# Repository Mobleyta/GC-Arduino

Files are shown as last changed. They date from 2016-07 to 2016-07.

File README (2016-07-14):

GasChromino Project

The GasChromino Program is an interface program that allows a PC/Mac/Linux system
to communicate with an Arduino that is connected to one or more gas chromatography
instruments.

The project consists of two main programming parts, the Arduino code that is uploaded to
an Arduino Uno (Rev 3) and the python code that is implemented on the computer. Serial
interface through a USB port allows the two programs to communicate.

Instructions for Installation, Configuration and Use:
  ./Instructions.docx
  ./Instructions.pdf

GC Analog Input on Arduino

 Program: ./ArduinoCode/GCDualInstrumentsSimul/GCDualInstrumentsSimul.ino
 Upload to Arduino using Arduino software
 
 This serves as a simple data capture routine from a
 1.0 V serial output of HP 5890 Series II gas chromatograph.

 Current Version: Complete with two channels, multiple runs,

 The circuit:
 See Frizzing diagram for description of circuit.  GCAnalogInputCircuitADS2ChanFinal.fzz

 Uses Adafruit breakout of ADS1115 Texas Instruments 16-Bit ADC

 Two different analog signals from GCs can be accommodated simultaneously

 Each signal has a separate Start/Stop Button
  Signal 1
    A0 input on ADS1115
    Start button on IO pin 9
    Stop button on IO pin 3
    Greed LED on IO pin 6
   Signal 2
    A1 input on ADS1115
    Start button on IO pin 8
    Stop button on IO pin 2
    Greed LED on IO pin 5

 Based upon Analog Input Example Created by David Cuartielles
 modified 30 Aug 2011
 By Tom Igoe

 GCDualInstrumentsSimul code written by T. Andrew Mobley, 9 Jul 2016
 based upon GCDualInsruments code

Serial Input from Arduino

  Program: ./PythonCode/GasChromino.py
  Run using python3
  
  This program serves as the master program linking multiple modules implementing various
  aspects of the program. Starting it loads a TK window that controls all program
  functions.
  
  A global variables file ./PythonCode/gcaglobals.py allows modification of the default
  settings of the program.
  
Circuitry Diagrams and Parts List

  The analog circuitry diagrams (Fritzing Files and png files), parts list:
  	Found in ./Circuitry

Example Data Sets

  Example data sets to allow users to explore processing procedures in program
	Found in ./Example Data Sets

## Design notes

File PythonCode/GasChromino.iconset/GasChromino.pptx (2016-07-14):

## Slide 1

GasChromino

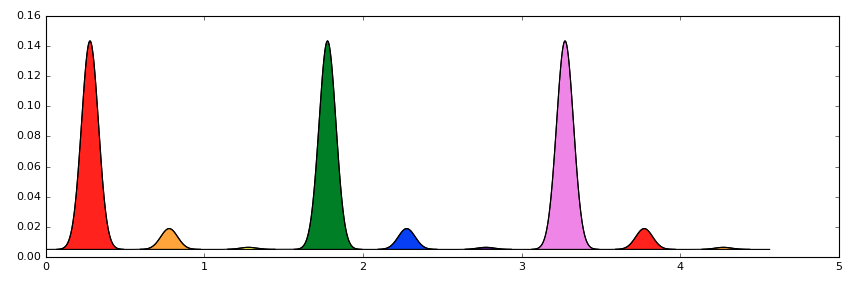
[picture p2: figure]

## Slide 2

GCino

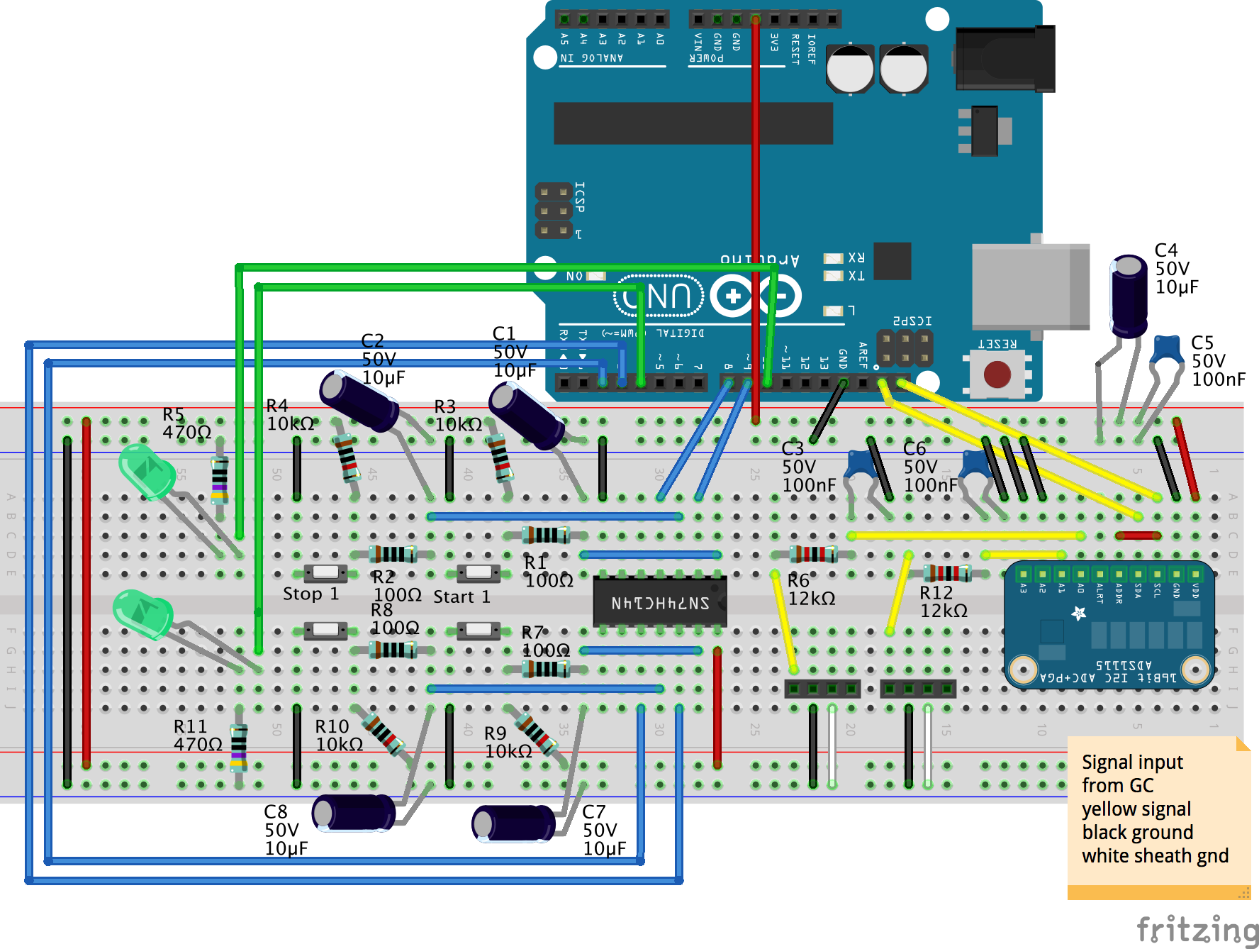
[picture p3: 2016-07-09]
Circuitry/CircuitryPictures/GCAnalogInputCircuitADS2ChanFinal_bb.png

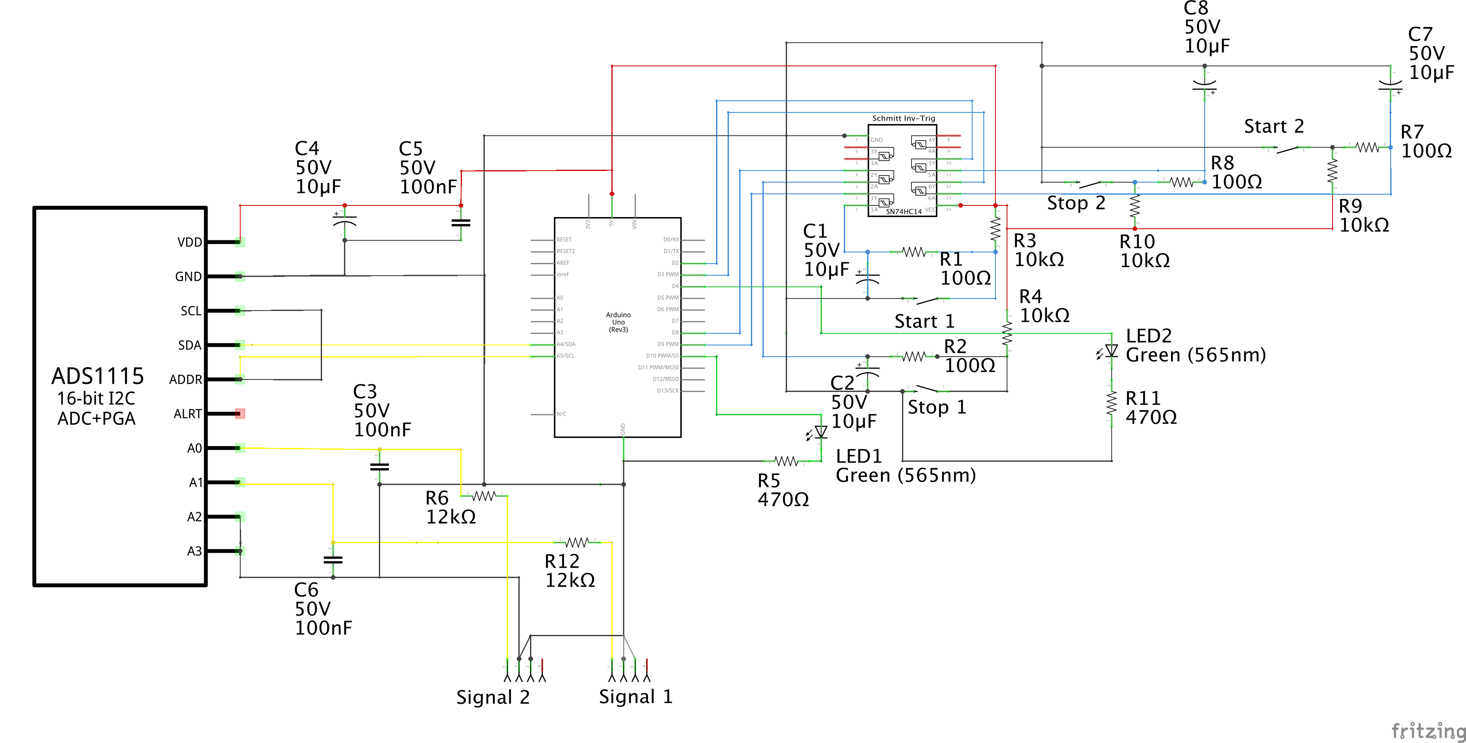
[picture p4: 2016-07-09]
Circuitry/CircuitryPictures/GCAnalogInputCircuitADS2ChanFinal_schem.png

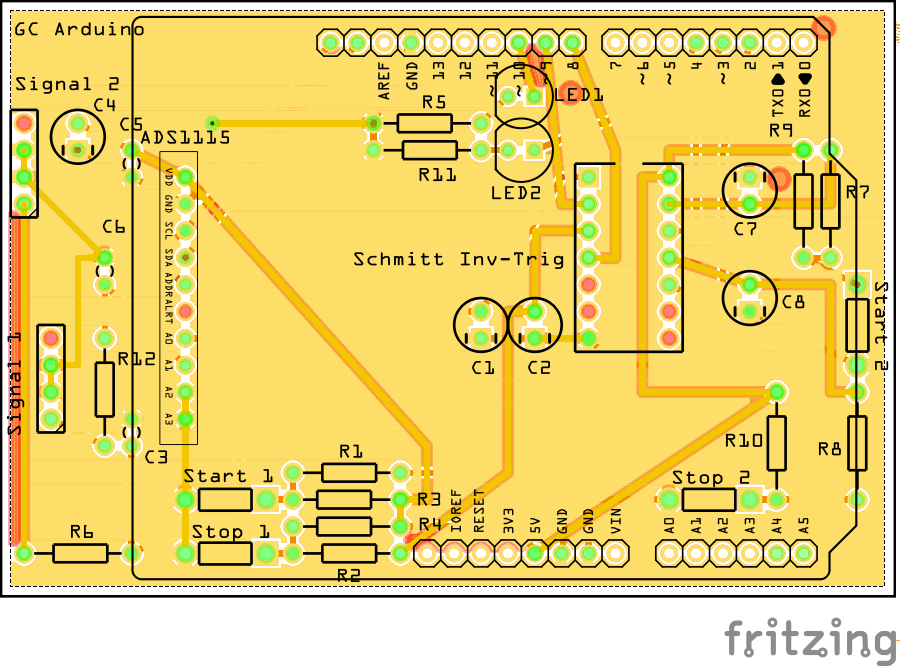
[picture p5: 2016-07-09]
Circuitry/CircuitryPictures/GCAnalogInputCircuitADS2ChanFinal_pcb.png

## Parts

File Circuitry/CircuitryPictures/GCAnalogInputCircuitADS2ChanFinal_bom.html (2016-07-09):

Label | Part Type | Properties
ADS1115 | ADS1115 16-bit ADC Breakout
C1 | Electrolytic Capacitor | package 100 mil [THT, electrolytic]; capacitance 10µF; voltage 50V
C2 | Electrolytic Capacitor | package 100 mil [THT, electrolytic]; capacitance 10µF; voltage 50V
C3 | Ceramic Capacitor | package 100 mil [THT, multilayer]; capacitance 100nF; voltage 50V
C4 | Electrolytic Capacitor | package 100 mil [THT, electrolytic]; capacitance 10µF; voltage 50V
C5 | Ceramic Capacitor | package 100 mil [THT, multilayer]; capacitance 100nF; voltage 50V
C6 | Ceramic Capacitor | package 100 mil [THT, multilayer]; capacitance 100nF; voltage 50V
C7 | Electrolytic Capacitor | package 100 mil [THT, electrolytic]; capacitance 10µF; voltage 50V
C8 | Electrolytic Capacitor | package 100 mil [THT, electrolytic]; capacitance 10µF; voltage 50V
GC Arduino | Arduino Uno (Rev3) | type Arduino UNO (Rev3)
LED1 | Green (565nm) LED | package 5 mm [THT]; leg yes; color Green (565nm)
LED2 | Green (565nm) LED | package 5 mm [THT]; leg yes; color Green (565nm)
R1 | 100Ω Resistor | tolerance ±1%; resistance 100Ω; package THT; pin spacing 400 mil; bands 5
R2 | 100Ω Resistor | tolerance ±1%; resistance 100Ω; package THT; pin spacing 400 mil; bands 5
R3 | 10kΩ Resistor | tolerance ±1%; resistance 10kΩ; package THT; pin spacing 400 mil; bands 5
R4 | 10kΩ Resistor | tolerance ±1%; resistance 10kΩ; package THT; pin spacing 400 mil; bands 5
R5 | 470Ω Resistor | tolerance ±1%; resistance 470Ω; package THT; pin spacing 400 mil; bands 5
R6 | 12kΩ Resistor | tolerance ±1%; resistance 12kΩ; package THT; pin spacing 400 mil; bands 5
R7 | 100Ω Resistor | tolerance ±1%; resistance 100Ω; package THT; pin spacing 400 mil; bands 5
R8 | 100Ω Resistor | tolerance ±1%; resistance 100Ω; package THT; pin spacing 400 mil; bands 5
R9 | 10kΩ Resistor | tolerance ±1%; resistance 10kΩ; package THT; pin spacing 400 mil; bands 5
R10 | 10kΩ Resistor | tolerance ±1%; resistance 10kΩ; package THT; pin spacing 400 mil; bands 5
R11 | 470Ω Resistor | tolerance ±1%; resistance 470Ω; package THT; pin spacing 400 mil; bands 5
R12 | 12kΩ Resistor | tolerance ±1%; resistance 12kΩ; package THT; pin spacing 400 mil; bands 5
Schmitt Inv-Trig | SN74HC14N | package DIP14 [THT]; variant variant 1; type SN74HC14N
Signal 1 | Generic female header - 4 pins | package THT; pin spacing 0.1in (2.54mm); pins 4; form ♀ (female); row single; hole size 1.0mm,0.508mm
Signal 2 | Generic female header - 4 pins | package THT; pin spacing 0.1in (2.54mm); pins 4; form ♀ (female); row single; hole size 1.0mm,0.508mm
Start 1 | Pushbutton | package THT; default state Normally Open; switching circuit SPST
Start 2 | Pushbutton | package THT; default state Normally Open; switching circuit SPST
Stop 1 | Pushbutton | package THT; default state Normally Open; switching circuit SPST
Stop 2 | Pushbutton | package THT; default state Normally Open; switching circuit SPST
Amount | Part Type | Properties
1 | ADS1115 16-bit ADC Breakout
5 | Electrolytic Capacitor | package 100 mil [THT, electrolytic]; capacitance 10µF; voltage 50V
3 | Ceramic Capacitor | package 100 mil [THT, multilayer]; capacitance 100nF; voltage 50V
1 | Arduino Uno (Rev3) | type Arduino UNO (Rev3)
2 | Green (565nm) LED | package 5 mm [THT]; leg yes; color Green (565nm)
4 | 100Ω Resistor | tolerance ±1%; resistance 100Ω; package THT; pin spacing 400 mil; bands 5
4 | 10kΩ Resistor | tolerance ±1%; resistance 10kΩ; package THT; pin spacing 400 mil; bands 5
2 | 470Ω Resistor | tolerance ±1%; resistance 470Ω; package THT; pin spacing 400 mil; bands 5
2 | 12kΩ Resistor | tolerance ±1%; resistance 12kΩ; package THT; pin spacing 400 mil; bands 5
1 | SN74HC14N | package DIP14 [THT]; variant variant 1; type SN74HC14N
2 | Generic female header - 4 pins | package THT; pin spacing 0.1in (2.54mm); pins 4; form ♀ (female); row single; hole size 1.0mm,0.508mm
4 | Pushbutton | package THT; default state Normally Open; switching circuit SPST

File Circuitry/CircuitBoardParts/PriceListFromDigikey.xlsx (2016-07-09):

Index | Quantity | Part Number | Description | Unit Price USD | Extended Price USD | USD
1 | 1 | 1528-1461-ND | ADS1115 16BIT ADC 4CH PROG GAIN | 14.95 | 14.95
2 | 5 | 493-5915-1-ND | CAP ALUM 10UF 20% 50V RADIAL | 0.26 | 1.3
3 | 3 | BC1084CT-ND | CAP CER 0.1UF 50V X7R RADIAL | 0.22 | 0.66
4 | 1 | 1659-1000-ND | ARDUINO UNO REV3 | 24.95 | 24.95
5 | 2 | 754-1265-ND | LED GRN DIFF 5MM ROUND T/H | 0.38 | 0.76
6 | 4 | RNF14FTD100RCT-ND | RES 100 OHM 1/4W 1% AXIAL | 0.10 | 0.4
7 | 4 | RNF14FTD10K0CT-ND | RES 10K OHM 1/4W 1% AXIAL | 0.10 | 0.4
8 | 2 | RNF14FTD470RCT-ND | RES 470 OHM 1/4W 1% AXIAL | 0.10 | 0.2
9 | 2 | S12KCACT-ND | RES 12K OHM 1/4W 1% AXIAL | 0.10 | 0.2
10 | 1 | 296-1577-5-ND | IC HEX SCHMITT-TRIG INV 14-DIP | 0.54 | 0.54
11 | 2 | 929400E-01-16-ND | CONN HEADER .100 SNGL STR 16POS | 1.09 | 2.18
12 | 2 | A28738-ND | CONN COVER BACK 12POS MT .100 | 2.24 | 4.48
13 | 2 | 102540-4-ND | 12 AMPMODU MT COVER DR .100CL | 1.33 | 2.66
14 | 2 | A19431-ND | CONN HEADER VERT 4POS .100 TIN | 0.18 | 0.36
15 | 4 | GH1368-ND | SWITCH PUSH SPST-NO 0.15A 5V | 2.07 | 8.28
16 | 2 | A34932-ND | CONN RECEPT 12POS .100 IDC GOLD | 5.80 | 11.6
17 | 2 | A31082-ND | CONN RECEPT 4POS 22AWG MTA100 | 0.27 | 0.54
 |  |  |  | Subtotal | 74.46

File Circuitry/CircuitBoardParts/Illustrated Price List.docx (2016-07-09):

Illustrated Price List

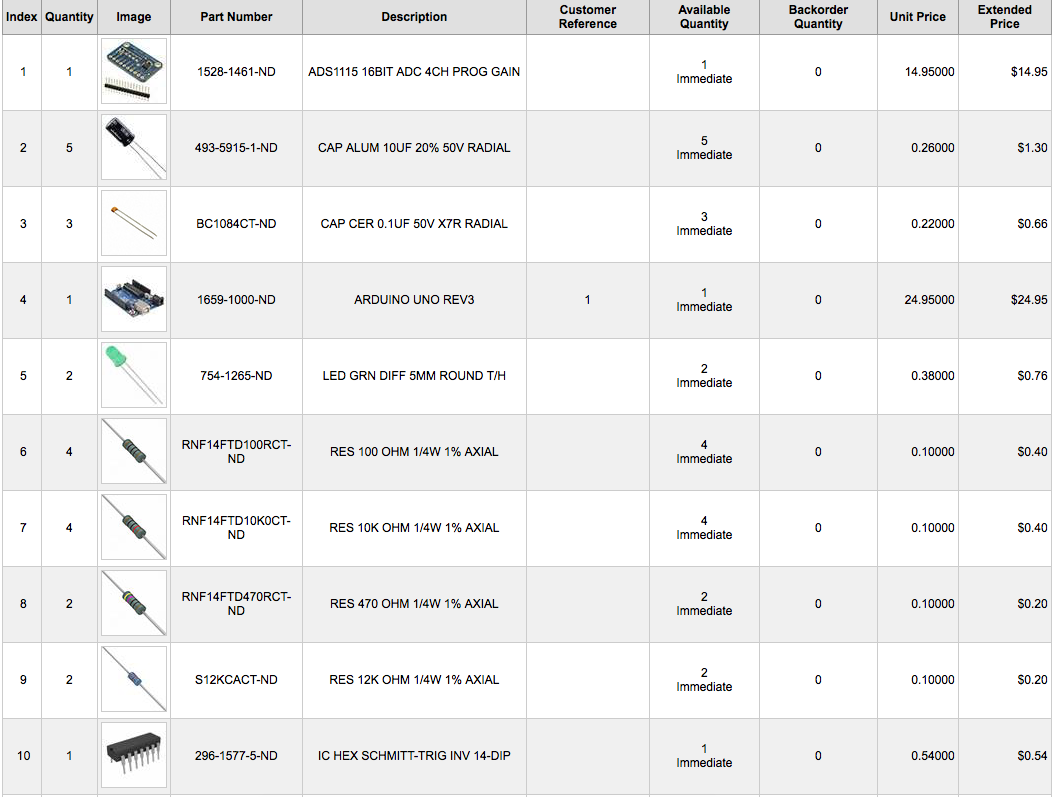
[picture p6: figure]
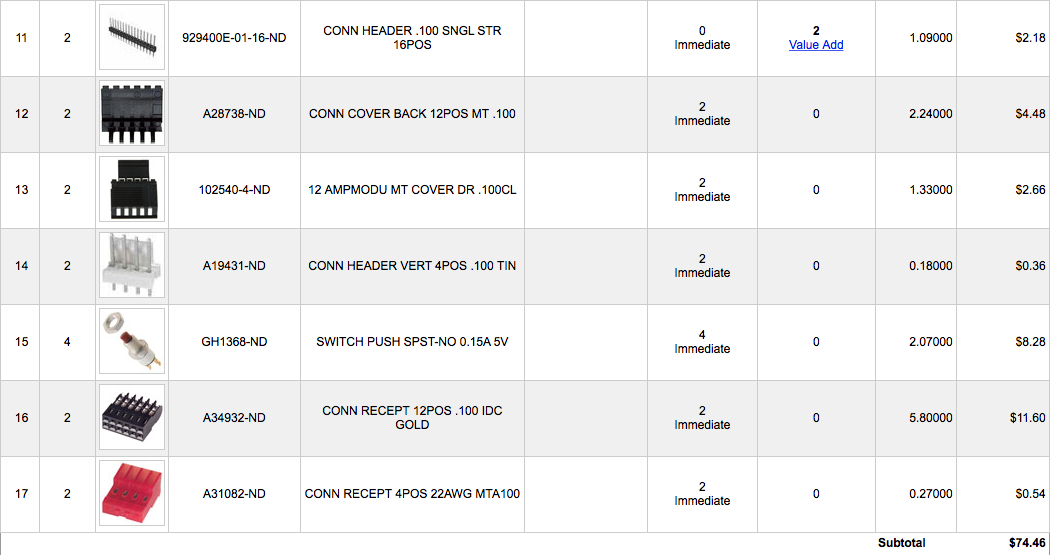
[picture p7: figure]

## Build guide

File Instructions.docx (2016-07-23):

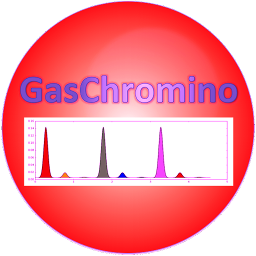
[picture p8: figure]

# GasChromino Program

## Description

The GasChromino Program is an interface program that allows a PC/Mac/Linux system to communicate with an Arduino that is connected to one or more gas chromatography instruments.

These instructions cover basic use including acquisition and processing of data. It also contains basic information for installation and configuration of the GasChromino program.

## Table of Contents

## Basic Use

This section outlines the general use of GasChromino to collect data from a single GC instrument. Use of multiple instruments is described below.

Upon opening the program, it should establish a connection to the Arduino, and it will show a successful connection in the lower right corner. If it fails to connect, see Connection to Arduino.

Prepare GC Prepare the GC by programming the temperature program, lighting the GC FID if necessary, etc.

Set time You should then set the Length of GC experiment in minutes to the length of time that the GC run will last. To account for differences in start times, make this slightly longer than the actual run-time of the GC to ensure that all data is acquired.

Set comment If you wish you could then set the Comment for Experiment that you want associated with this experiment.

Start experiment To prepare the Arduino for collecting data, click on the button Prepare Arduino. This stores the comment and sends the experiment time to the Arduino, but does not actually start the GC.

Make injection and Start data collection Once the GC is ready:

1. Make your injection
2. Start the GC by hitting the GC Start button
3. Start data collection by hitting the Start button on the GCArduino.
  a. There is no harm in starting the GC and Arduino in the opposite order as long as they are started close in time to each other
  b. Future implementation may involve remote start of the GC using the Arduino, but this is not yet implemented.

Observe data collection Once the Arduino start button has been pressed, the program will switch to the Live Data window and show the data as it arrives to the computer.

Stopping data collection The data collection will automatically stop when the time of the experiment entered earlier is reached. Alternatively, the stop button on the Arduino will also stop data collection.

Stopping the GC Stopping the GC is done in the normal fashion using the GC stop button. The GC is not and cannot be stopped by the Arduino.

## Peak Processing

The GasChromino program can process GC traces using an automatic peak finding routine, but the user can also manually indicate peaks by marking the beginning and end of the peak. In both routines, the GC finds a baseline of those data points not indicated as peaks and uses this baseline to correct the area of the peaks. Finally, a normalized area is provided for each peak versus the total area of peaks. The user can remove all peaks or individual peaks as desired.

Automatic Processing The automatic processing routine utilizes two parameters to look for the start of peaks in comparison to a running baseline. If the slope at two points is greater than the Peak Start Gradient Threshold for two consecutive points (slope at point “b” and slope at point “c”) and the value of the intensity at the second point (point “b”) is greater than the Peak Start Threshold, a peak start is detected and marked at the previous point (point “a”), otherwise as long as point “b” is near in value to the running baseline, it is added to the running baseline and the routine moves to the next point. Once a peak start is detected, the routine finds to the top of the peak and detects the end of the peak in a similar fashion. For details of the peak detection routine, see the appendix on Processing details.

Thus, the two parameters to manipulate to change the automatic processing routine are the Peak Start Threshold and Peak Start Gradient Threshold. By making either of these values smaller, more peaks will be detected, and the user can use his or her own data or the Sample Data Trace provided to experiment with this routine. Changing the two parameters at any point prior to stopping an experiment will result in those values being incorporated in the routine. Alternatively, the data can be reprocessed subsequent to acquisition by hitting the Find and Integrate Peaks button.

Manual Processing The manual processing routine can be done after automatic processing to either add or subtract peaks. Manual processing determines the baseline used to correct peak areas by using all points not included in peaks. Thus, it is very important that all peaks are included when using manual processing, otherwise the baseline correction can be quite faulty. This is especially true for large peaks like the solvent [see below for a method to remove solvent peaks from the listing of peaks].

Picking peaks To carry out manual processing to add peaks after most are detected using automatic processing, the user can Ctrl-Click and drag where the initial click is at the starting point and the release of the click is the ending point. Small red arrows on the trace indicate the beginning and end of indicated peaks. Processing of the picked peak is then effected by clicking on the Integrate Picked Peaks button. Additional peaks can then be added as desired either before or after clicking on the button.

Deleting peaks Individual peaks can be removed from the peak list by shift-clicking while the cursor is within the peak area. This will remove the peak from the list and renormalize the peak areas. However, it does not add those points to the baseline calculation and thus is a way to remove large peaks from the integration and not affect the baseline.

Copying peaks to clipboard The list of peaks can be copied by clicking on the button Copy Peaks to Clipboard. They can then be pasted into another application (Word, Excel, etc.).

Tutorial for Algorithm to Pick Peaks The following is a quick tutorial utilizing the provided data sets to explore the pick peaking routines.

1. Open the example data set Example Data 1.

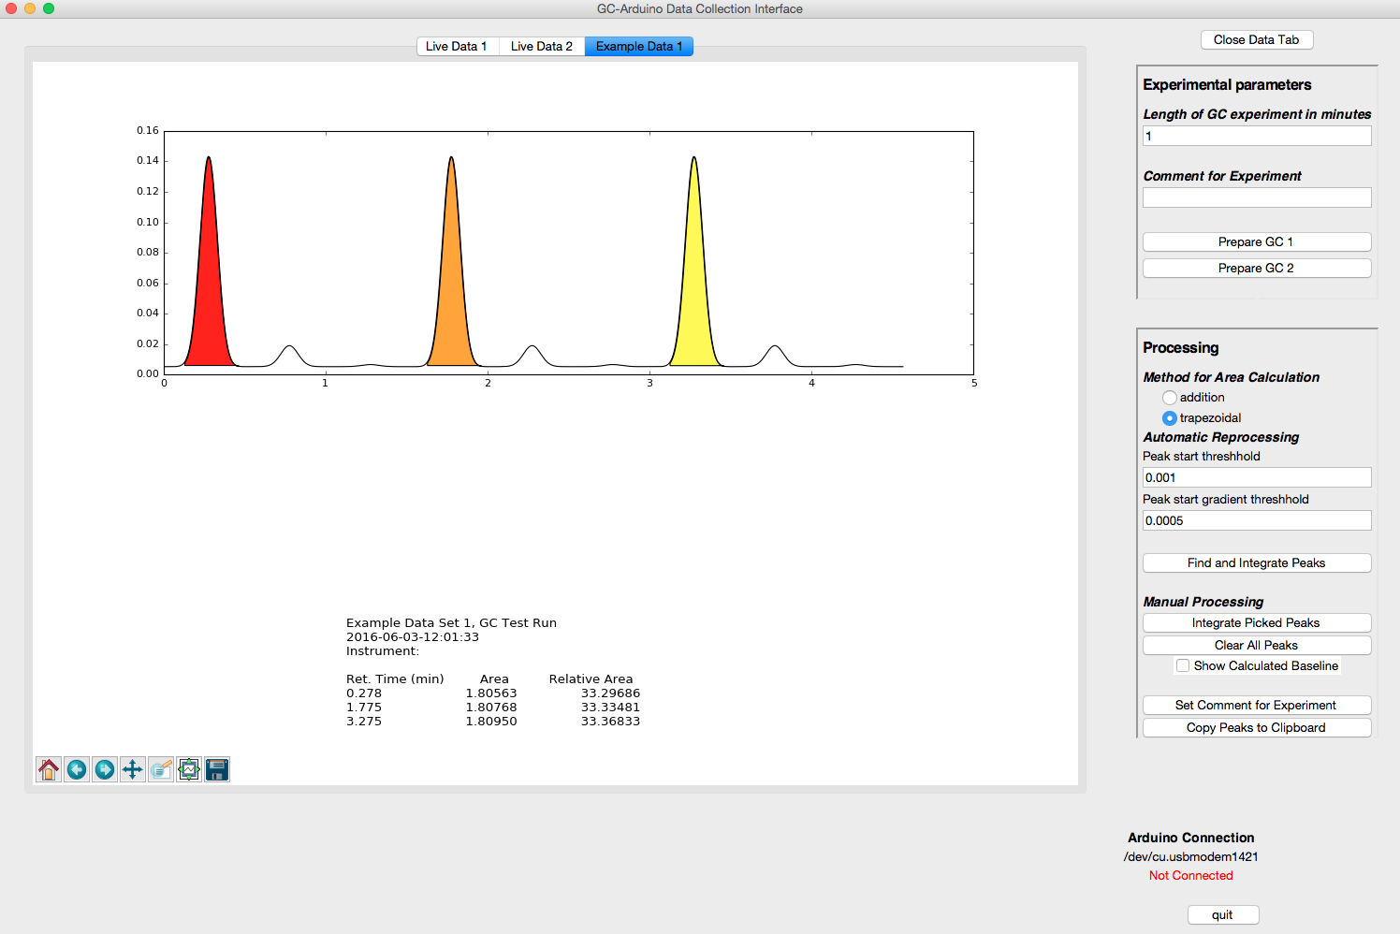
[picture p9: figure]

2. Change the Peak gradient start threshold to be 0.0001 (change 5 to 1)
3. Click on the Find and Integrate Peaks button

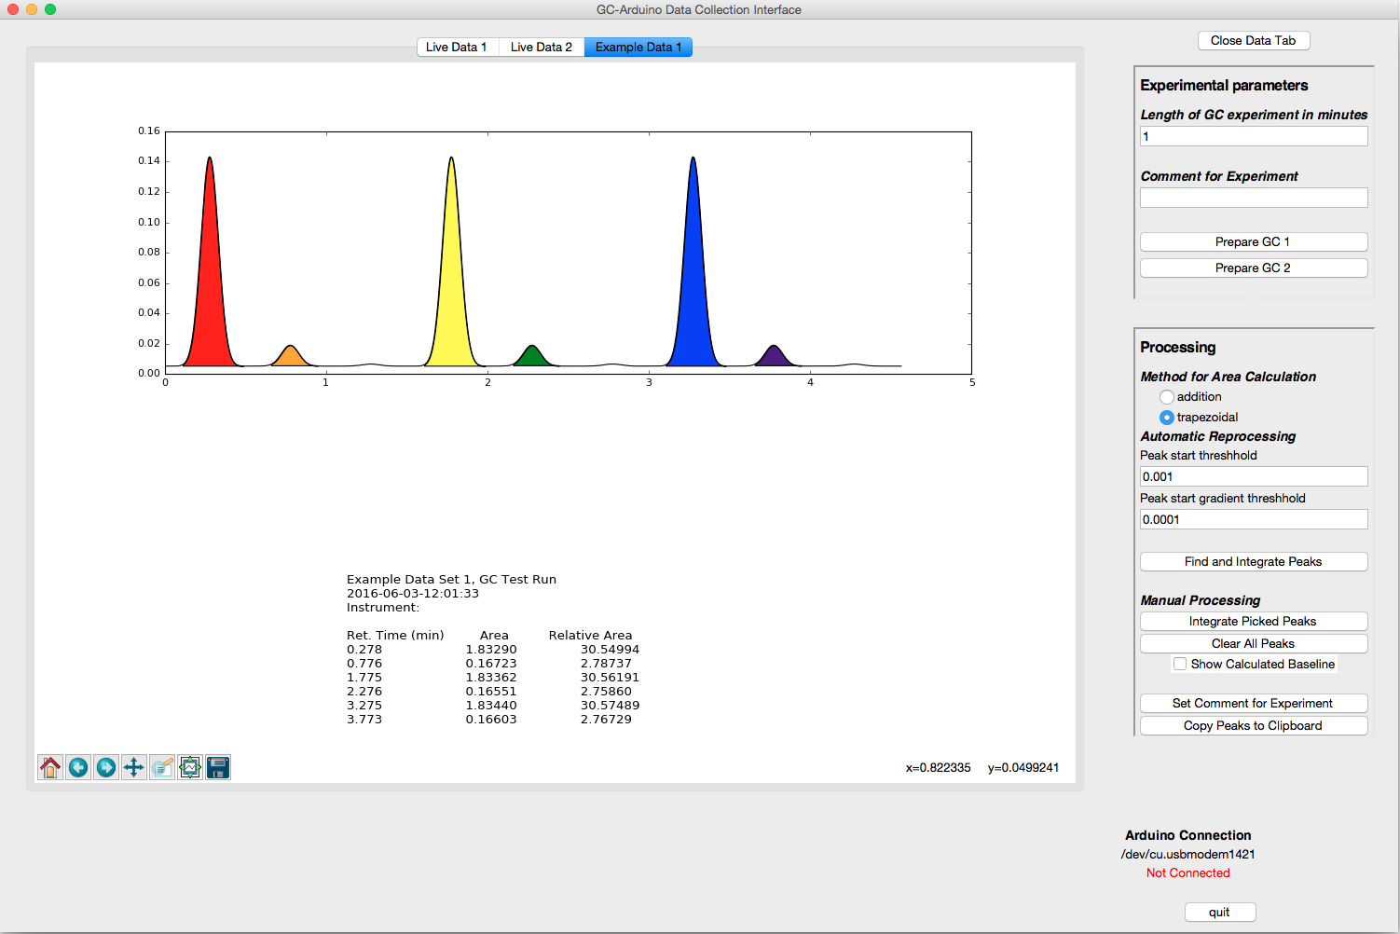
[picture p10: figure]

As you can see, the middle size peaks have been detected, but not the smallest peaks. Moreover, closer inspection of the middle size peaks will show imperfections in the baseline detection in this dataset.

4. Pick the Zoom to rectangle tool in the lower left corner of the data window
5. Draw a rectangle around the orange peak and the small peak to its right and release to zoom to that area.

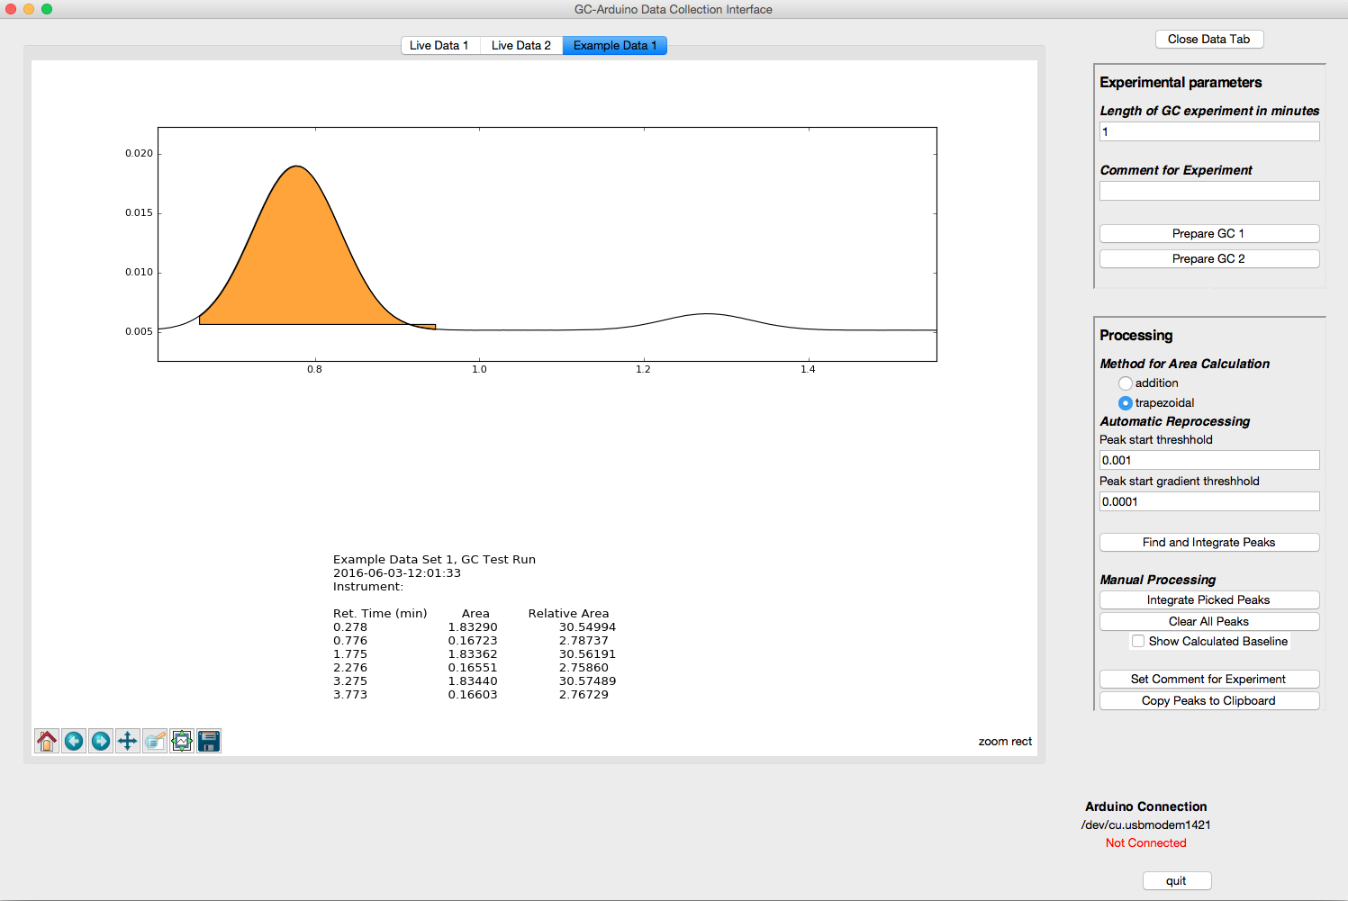
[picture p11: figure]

Note the small errors in the area indicated for the orange peak. The horizontal line of the bottom of the peak indicates the baseline that is being used to correct the integration of the orange peak. A small portion of the peak is missed at the beginning of the peak and because of that the baseline calculated by the automatic routine is a bit high.

One can fine-tune the peak detection further to fix small errors like this. By dropping the Peak start threshold and the Peak start gradient threshold, the definition of the baseline is refined and the shape of the peak integration improves.

A good way to understand better how the two thresholds are affecting the baseline and peak detection routine is to view the baseline (by default it is turned off). The toggle is just under the Clear All Peaks button.

6. Toggle the baseline by clicking on the checkbox Show Calculated Baseline.    One can see how the detection of the beginning of the orange peak is late, resulting in a baseline that lags behind the GC trace at the beginning of the orange peak. Due to this it calculates a baseline that is actually higher than it should be resulting in the portion of the peak below the baseline at the tail of the orange peak.  Additionally, because the smaller peak on the right is so broad, the gradient threshold is not sufficiently low to detect it and the baseline ends up as a ghost of that peak.  The peak detection is significantly improved by lowering the two thresholds. Explore the effects of changing each of the thresholds on the peak detection routine.

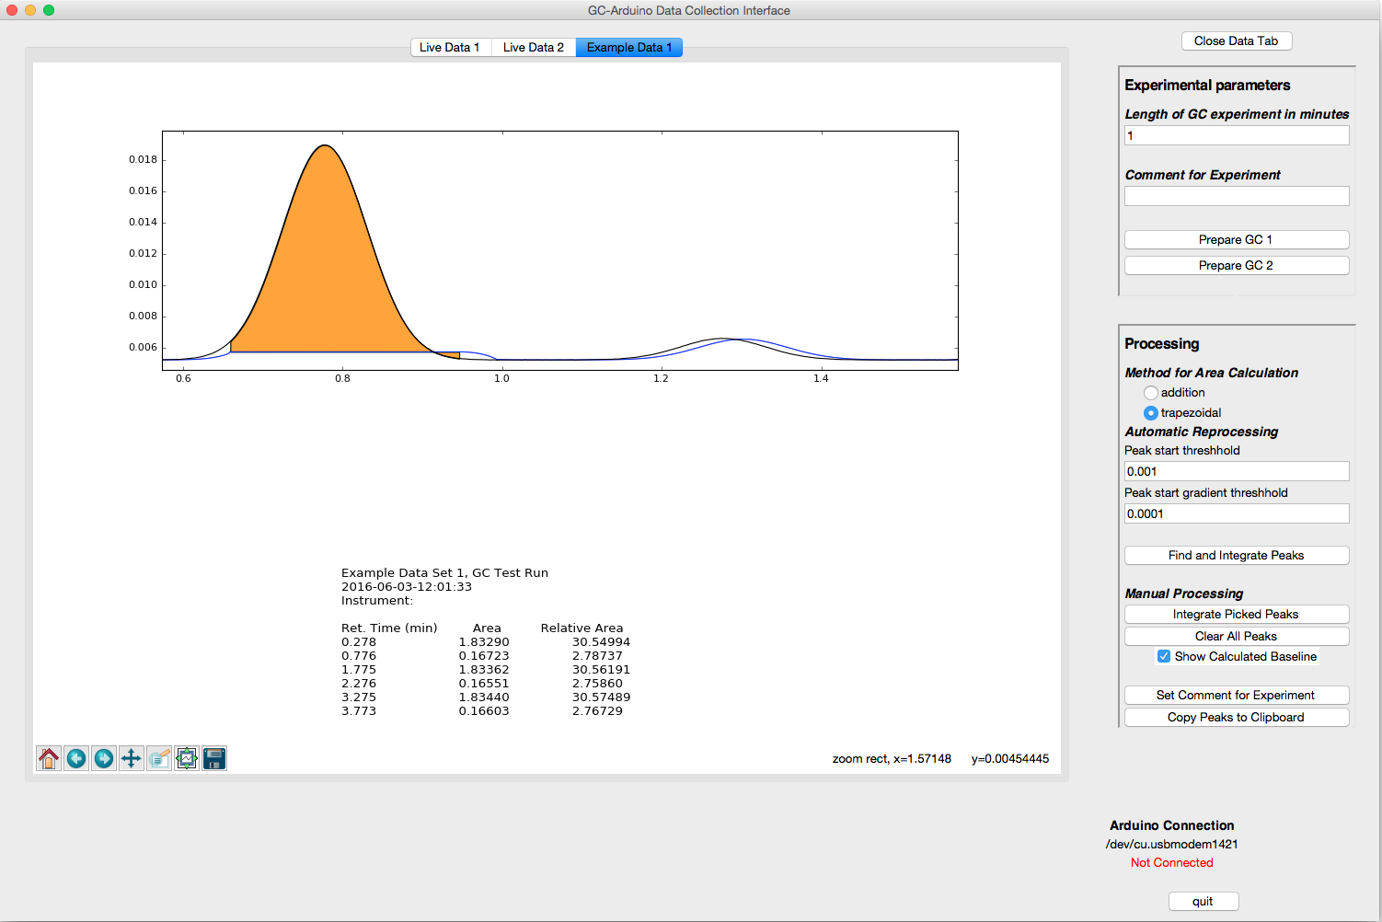
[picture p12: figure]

7. Set both the Peak start threshold and the Peak start gradient threshold to 0.00001, hit Find and integrate peaks, and re-zoom.   Now, the small peak is also picked and the baseline is much better defined as well.  As a measure of the accuracy of the GasChromino and this peak-picking routine, the ratio of the three peaks in a grouping should be 10:1:0.1.  This methodology will not work particularly well with very small peaks, however. This is especially true when the baseline is sloping due to smaller peaks riding on the trailing edge of a much larger (e.g. solvent) peak. A more realistic dataset with very small peaks is provided as Example Data 3.

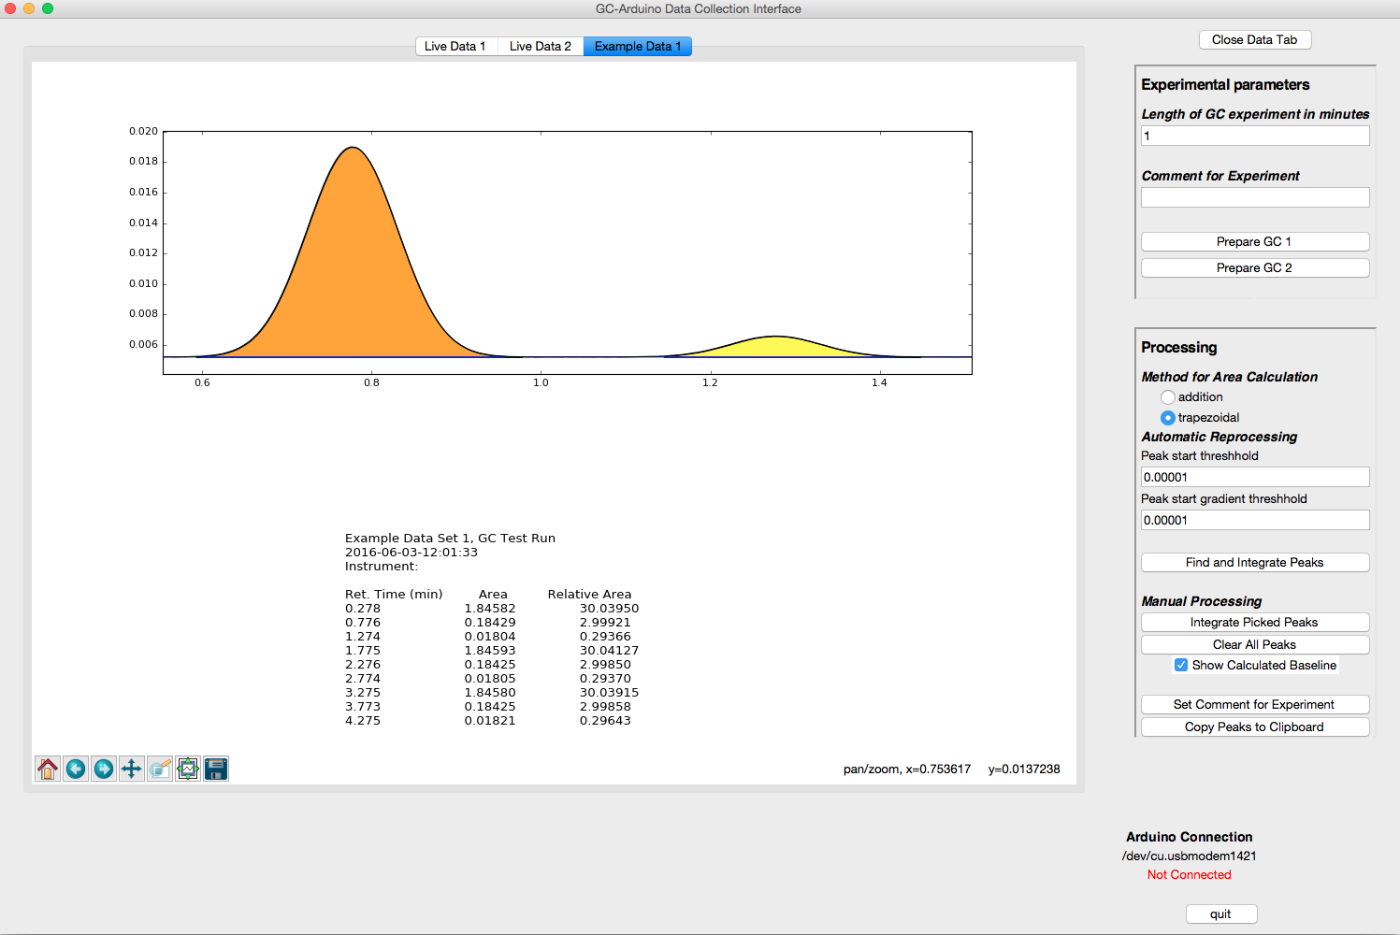
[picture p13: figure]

8. Open Example Data 3. Zoom near the baseline from 2 to 3.5 min and you will see small peaks. It may take multiple zooms to get a picture approximating that shown below.   With careful choice of the automatic detection parameters, one could eventually pick these peaks in this particular dataset; however, it is much easier to pick them manually.

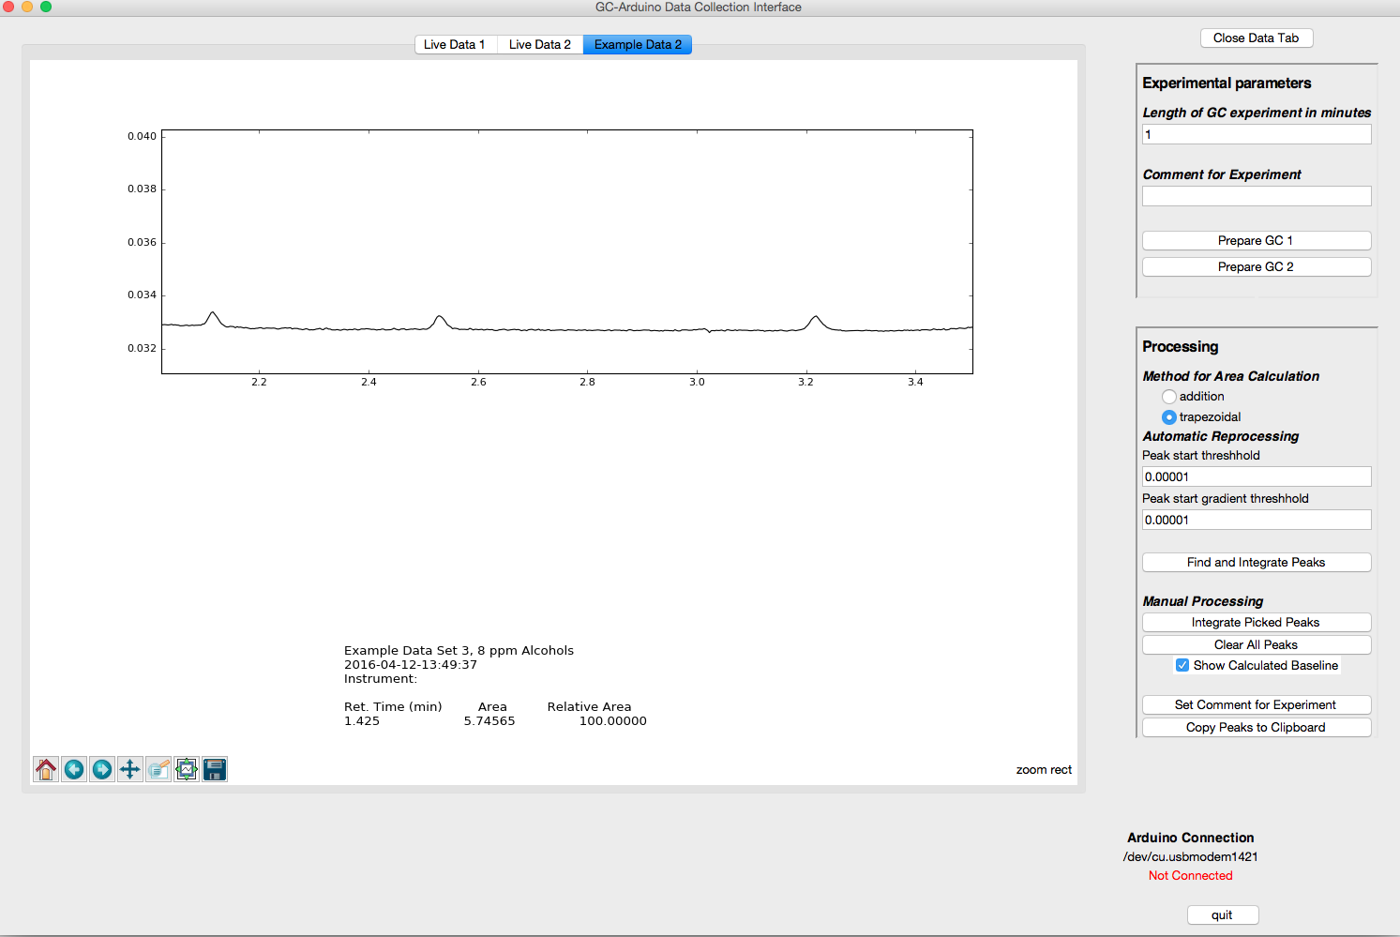
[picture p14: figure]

9. Make sure that you de-select the zoom to rectangle tool and then Ctrl-click and drag from left to right of the left-most small peak, releasing the click when you reach the point you decide is the right-most end of the peak. Repeat for the following peaks.

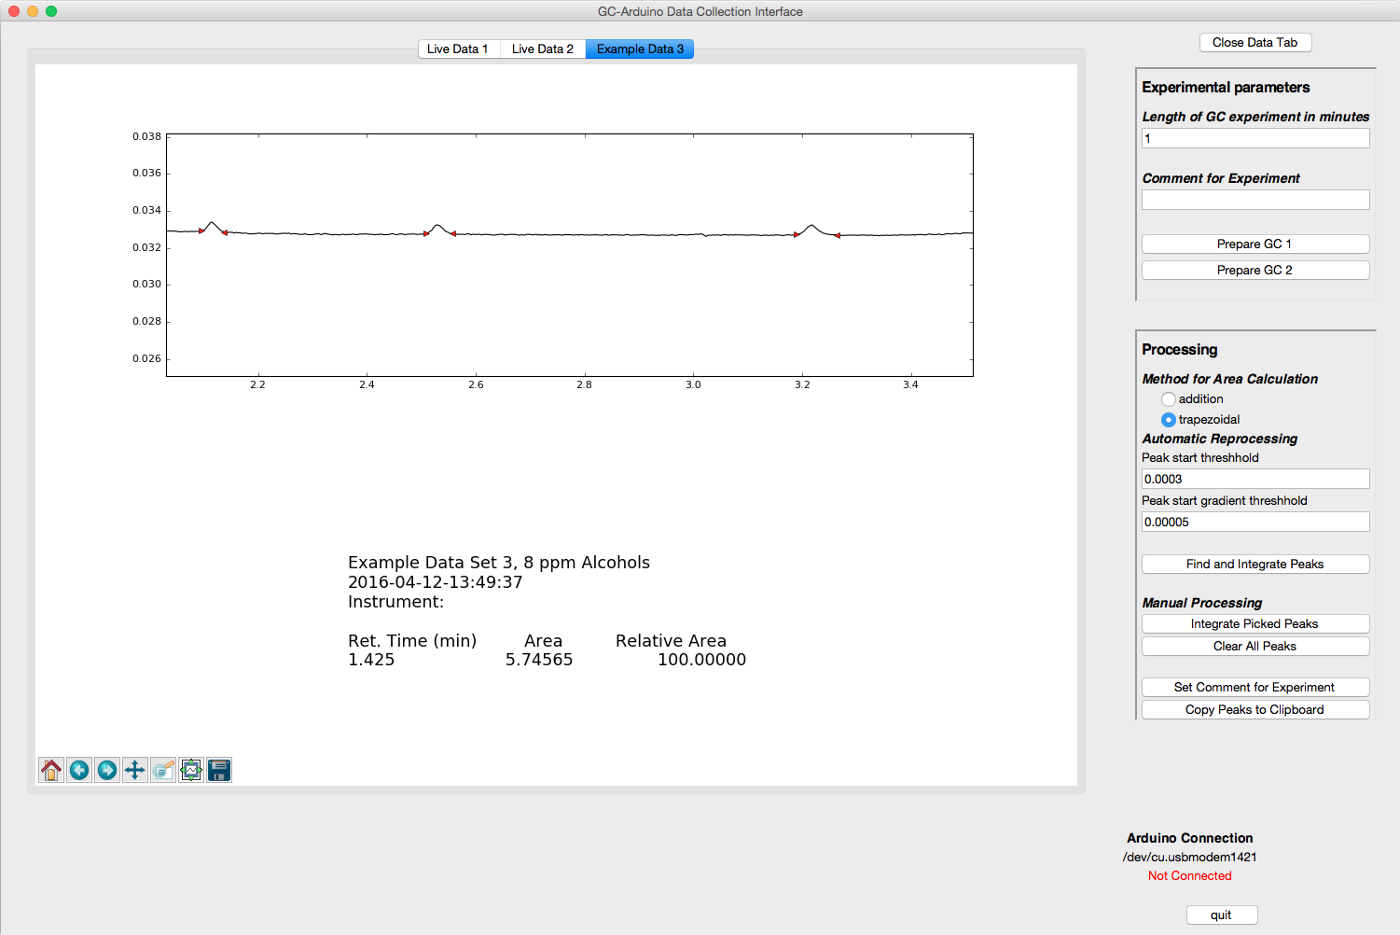
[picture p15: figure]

Note the small red triangles at the left and right of the small peaks. These mark the chosen left- and right-limits of each peak.

10. Click on Integrate Picked Peaks button to integrate the peaks. The screen will reset to see the entire GC trace.
11. After re-zooming to the region of interest (including the solvent this time) with baseline on, one can see the results of the picked peaks.    It is clear that the baseline determination is struggling due to the presence of the very large peak. As long as the large peak is not of interest, the program can follow the baseline of the trailing peak by telling it to limit the baseline calculation to near the area of interest.

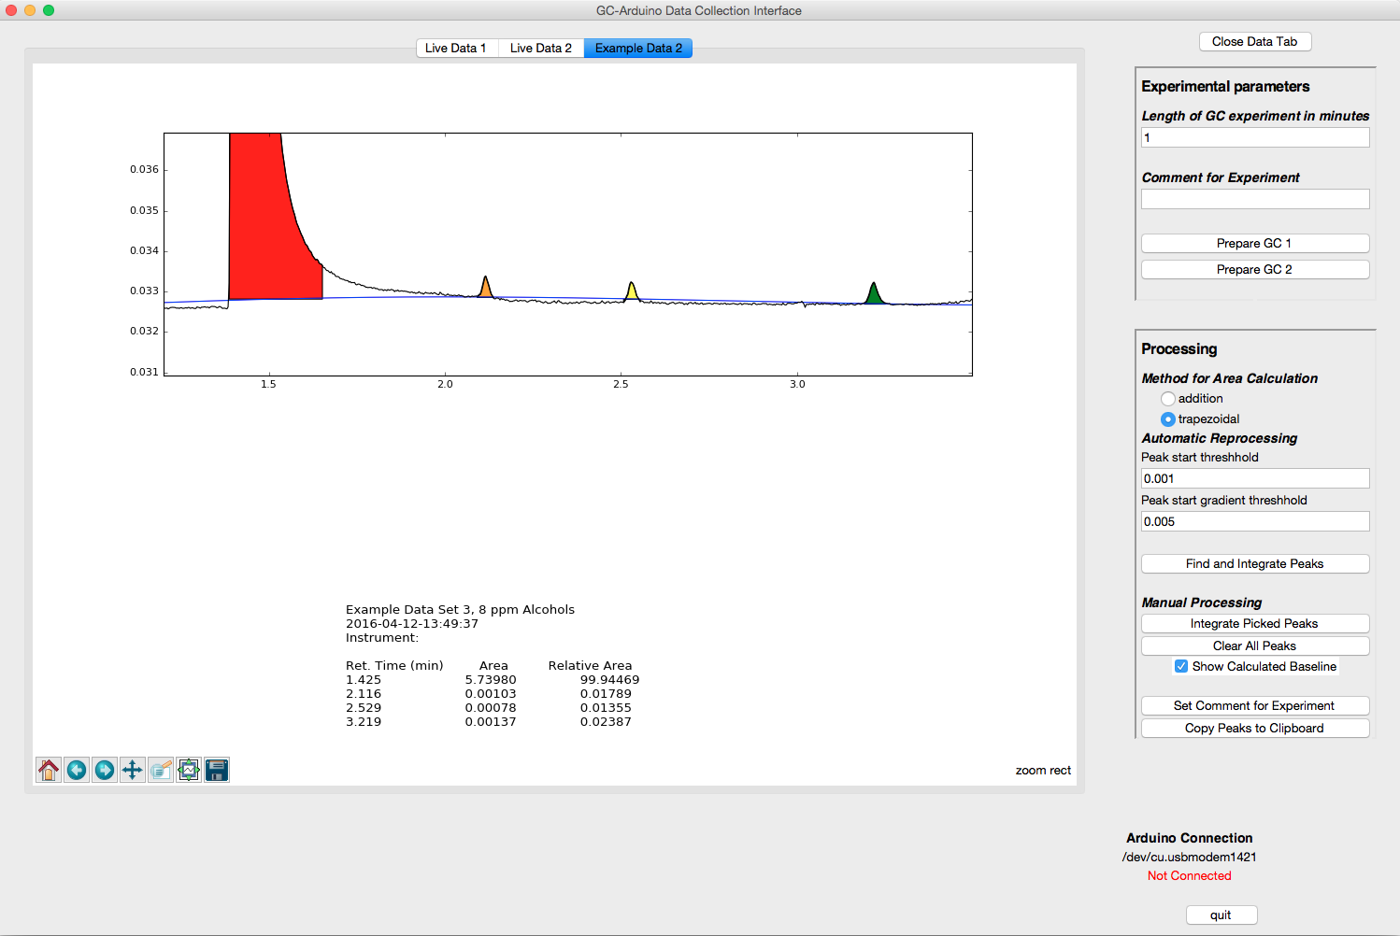
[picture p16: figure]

To correct, complete the following steps.

12. Hit Clear All Peaks button
13. Hit the Find and Integrate Peaks button to automatically detect the solvent (alternatively, one can simply reload the data by reopening it).
14. Re-zoom to the area of interest, this time from about 1.9 min to 4.1 min.
15. Pick the three peaks of interest, but also the little glitch at about 3.0 min and the very broad peak at about 3.5 min. It is important to identify all peaks so they do not get counted as baseline.
16. To limit the baseline calculation Ctrl-b Click and Drag (hit Ctrl+b at the same time you are clicking and dragging from the left side of the trace to the right).  You should have a picture that looks like this.   The Blue triangles mark the beginning and end of the baseline area. Peaks will not be included in the baseline calculation.

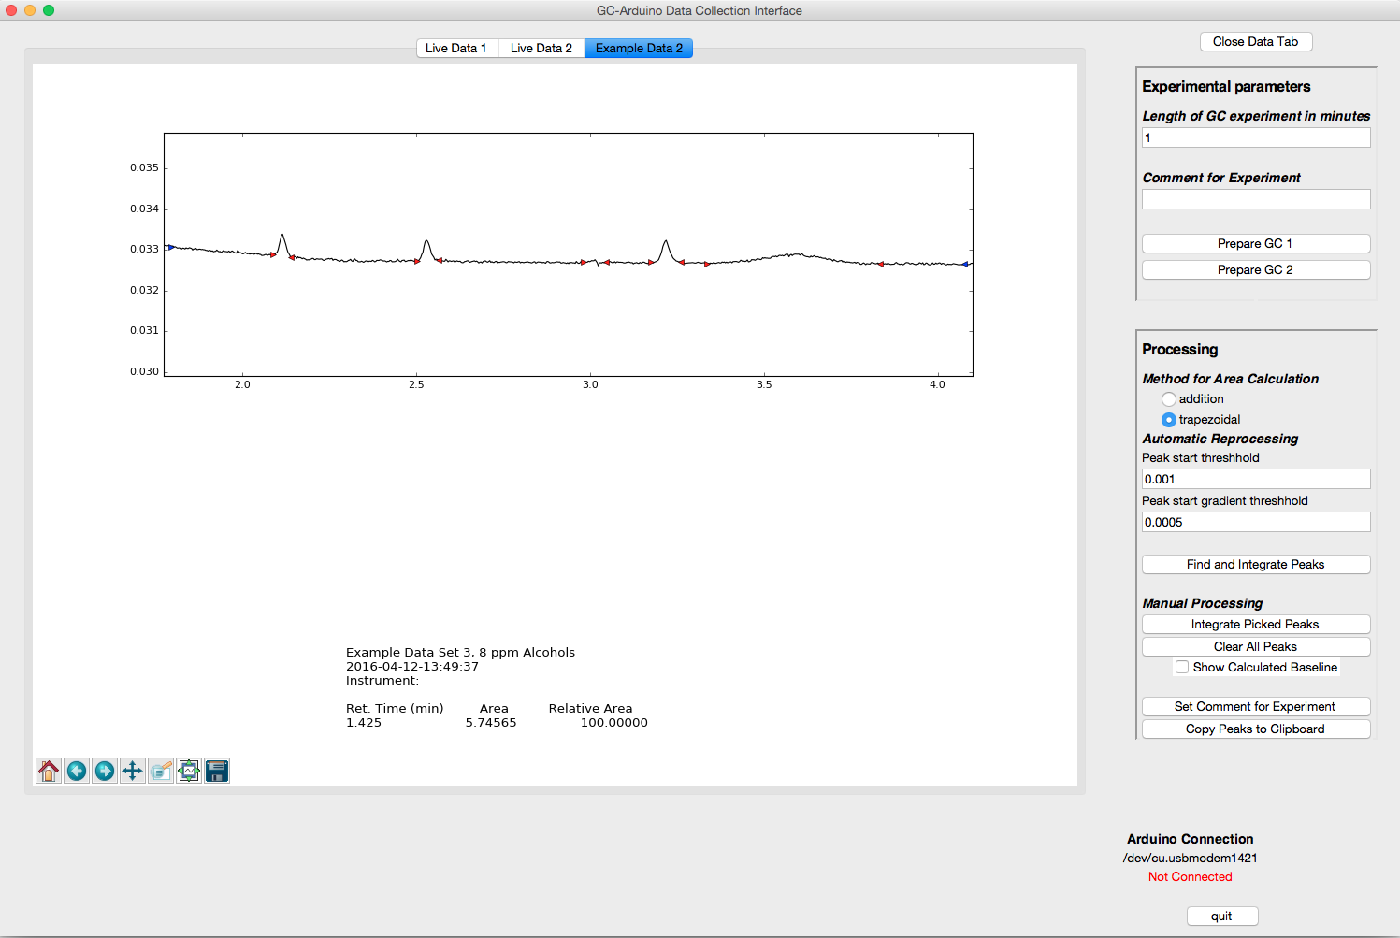
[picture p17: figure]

17. Click on integrate picked peaks and turn on the baseline (if it is not already). Re-zoom to the area of interest.   One sees a much better fit of the baseline (in the area of interest), and the three peaks that nominally are 1:1:1 are much closer in area. If one looks at other parts of the GC trace, the baseline fit is very poor since the fit is based solely upon the single region that you have defined.

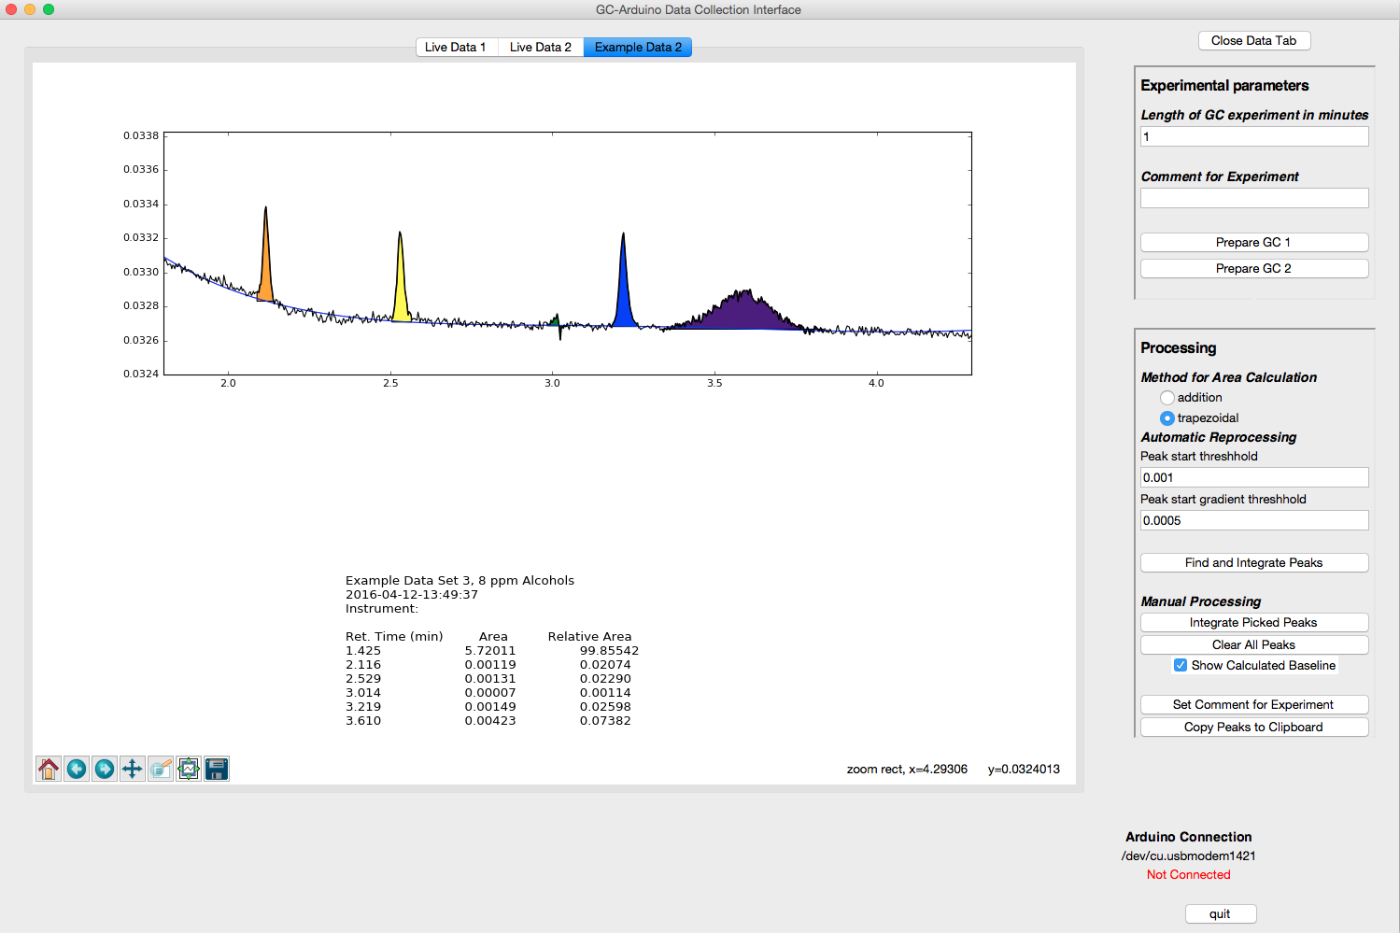
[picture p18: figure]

Presuming that the desired ratio is actually between the three small peaks and that the area of the solvent peak, the glitch and the broad peak are not of interest, one can delete the solvent peak and the other two.

18. Remove the glitch and the broad peak by Shift-Clicking while the cursor is on the peak to remove. You will need to re-zoom as the display resets after each deleted peak.
19. To remove the solvent peak, first, reset the trace by clicking on the home button in the toolbar:
20. Shift-Click on the solvent peak and the peak will be deleted, the areas updated, and the trace re-plotted. Below is the zoom of the three small peaks.

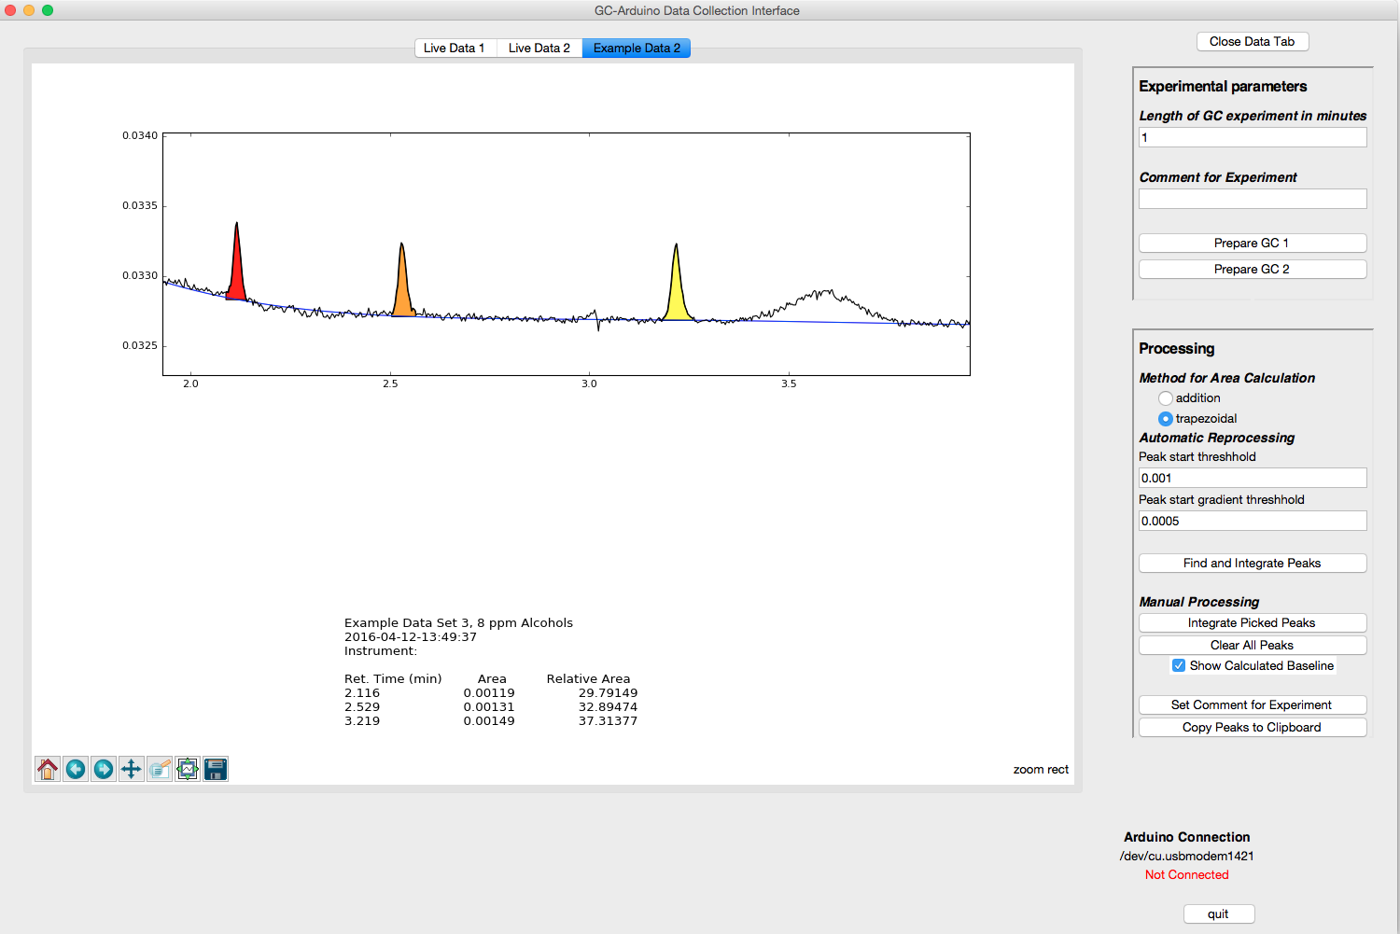
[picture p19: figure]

A third data set that has large (solvent), medium (peaks of interest), and small (impurities) peaks is provided as Example Data 2. Explore the peak-picking routines to practice with this data set.

## Using Multiple Gas Chromatography Instruments

The GasChromino program is capable of handling two GC instruments at once, collecting data from both of them at the same time. Overall, the process is similar to that for collecting data from a single instrument, but one can start both instruments and observe data from each. Each time an instrument finishes a data collection, the data will be transferred to a new tab and automatically processed. You can switch back to the Live Data of the other instrument, other data tabs, or perform processing while the program is collecting data from the other instrument.

Hopefully, the two GCs are well labeled to make choosing the instrument in the program easier. See Configuration below for a description of how to change the labels on the Prepare Channel 1 and Prepare Channel 2 buttons to make them match your situation.

Prepare GC Prepare either (or both) GCs by programming the temperature program, lighting the GC FID if necessary, etc.

Set time You should then set the time of the experiment to the length of time that the GC run will last. To account for differences in start times, make this slightly longer than the actual run-time of the GC to ensure that all data is acquired.

Set comment If you wish you can then set the comment that you want associated with this experiment.

Prepare Arduino To prepare the Arduino for collecting data, click on the button Prepare GC 1 or Prepare GC 2. This stores the comment and sends the experiment time to the Arduino, but does not actually start the GC.

Differences for multiple instruments When using two GCs, it will be necessary to set the parameters twice (if the time and comment parameters are to be different) and hit the Prepare Channel 1 or 2 for each instrument. Both instruments can be prepared prior to actually starting a run.

Thus, the order of steps is:

1. Set Time for GC 1
2. Set Comment for GC 1
3. Hit prepare button GC 1
4. Set Time for GC 2
5. Set Comment for GC 2
6. Hit prepare button GC

Make injection and Start data collection on first GC

Once the first GC is ready:

1. Make your injection on one of the two GCs
2. Start that GC by hitting its Start button
3. Start data collection by hitting the corresponding Start button on the GasChromino.

Observe data collection on first GC Once the Arduino start button has been pressed, the program will switch to the Live Data window for that GC and show the data as it arrives to the computer.

Make injection and Start data collection on second GC

Once the second GC is ready:

1. Make your injection on the second GC
2. Start that GC by hitting its Start button
3. Start data collection by hitting the corresponding Start button on the GasChromino.

Observe data collection on first GC Once the Arduino start button has been pressed, the program will switch to the Live Data window for that GC and show the data as it arrives to the computer.

Stopping data collection for either instrument The data collection will automatically stop when the time of the experiment entered earlier is reached. Alternatively, the stop button for either of the GCs on the Arduino will stop data collection for that GC.

Stopping the GC Stopping the GC is done in the normal fashion using the GC stop button. The GC is not and cannot be stopped by the Arduino.

## Connection to Arduino

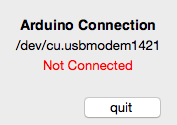
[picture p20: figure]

If the program does not automatically recognize the Arduino, a pop-up window will appear indicating this and the bottom right corner of the main window will indicate that the Arduino is not connected. Additionally, the port that the program is attempting to connect to is provided. In the case shown below, this port is /dev/cu.usbmodem1421.

The failure to connect may mean that the Arduino USB cable is connected to the wrong USB port or not connected at all.

### Troubleshooting

1. Check that the USB cable is connected to the Arduino and the computer
2. If both cables were connected, check that the port that the program is connecting to is correct.
  a. One can determine this port using the Arduino software
  b. One can also see which ports are in use by choosing the menu item Arduino Communications, submenu Set Arduino Port  This will provide a list of the ports that were in use when the program started.
3. If the Arduino is simply connected to a different port, one can use the menu item Arduino Communications/Connect to Arduino to attempt to reconnect.
4. If the cables were not connected, the Arduino port will not show up in the list of ports. [Currently the program only tests the ports upon start-up. Newly implemented: now can recheck, needs error testing.]
  a. If the port name is correct, one can still use the menu item Arduino Communications/Set Arduino Port even though the port name does not show up.
  b. If the port name is not correct, use the Recheck Port List submenu item. The port name should now show up and can be chosen.
  c. If the port still does not show up, there may be a problem with the Arduino, or possibly a bad cable. One could try resetting the Arduino and/or changing out the cable.

## Installation of GasChromino Software

For general use, a zip file that includes everything necessary to run GasChromino is available from XXX.XXX. After downloading the zip file appropriate for your OS (currently only available for Mac OS X Yosemite), unzip and run the included gcSetup batch file. The gcSetup batch file will ask several questions regarding file placement and copy the files to the correct locations. After installation, the zip file and the initial directory it was unzipped into can be deleted. Details about individual OS’s follow.

Prior Installations The gcSetup program recognizes when the application has been already installed, and checks to make sure that you want to reinstall. It will then overwrite files for the application and support files. Data files should not be affected, although the environment variables pointing to data file directories may be changed depending upon user choices during installation.

### Mac OS X Installation

App Installation Directory The default location for installation of GasChromino is in the /Applications directory. This allows the program to be utilized by all users on the computer. If this is not desired, the user can type in another directory location. There is little error-checking at this point for this directory, so be careful.

Data Files Directory The GasChromino program can be set up to have either individualized data directories or a global data directory, depending upon the needs of the laboratory environment.

Global Data Location The default global data location is in /Users/Shared/Documents/GasChrominoData but this could be anywhere, even a networked location. The gcSetup program recognizes pre-set locations based upon prior installations and suggests default locations. The user can accept either of these or specify another directory.

Local Data Location By utilizing the prefix $HOME followed by a directory path that would (will) appear within an individual’s directory, the program will set the data path to each user’s home directory. Upon initial running of the program, if this directory is not detected, it is assumed that the program has not yet been run and the directory is created and the Example Data Sets are placed in it.

Support Files Directory A directory is specified by the program that contains files utilized by the program. These support files include the Instructions (this document) and a configuration file (GasChromino.cfg). If on the first time that GasChromino runs it does not find these files (most likely gcSetup has not been run), then it will default to the version supplied with the program, and ask the user to edit the file to personalize the installation. This behavior can be repeated by deleting the GasChromino.cfg file.

Global Support Files Location The default global support files location is in /Library/Application Support/GasChromino but this could be any valid path. The gcSetup program recognizes pre-set locations based upon prior installations and suggests default locations. The user can accept either of these or specify another directory. In general, when the program is going to be used to control an instrument, a single GasChromino.cfg file should be utilized.

Local Support Files Location If the program is going to be used only as a data station on the installed computer, then individuals may want to customize their individual GasChromino.cfg. By utilizing the value $HOME in place of the directory path for the personalized support location, gcSetup will create the directory and place the Instructions.pdf file in it. GasChromino.cfg is then copied by the GasChromino app into the individual user’s support directory the first time the program is run (or whenever it does not find a valid GasChromino.cfg file).

Environment Variables The environment variables that control GasChromino are set within the program’s Info.plist file (with default installation found in /Applications/GasChromino.app/Contents). This file is modified by the gcSetup routine upon initial installation.

Advanced Environment Setup The gcSetup routine also sets several bash environment variables using the initial user’s $HOME/.bash_profile file. Should the program need to be run from Terminal, these environment variables provide the necessary information. These variables are only set for the initial user, should all users need to run the program utilizing Terminal, these lines should be modified and added to each individual’s $HOME/.bash_profile or in /etc/profile or /etc/bashrc file. This more advanced setup is left to the end-user, as it will vary from installation to installation (and if you are fiddling with using it in Terminal, you probably know what to do anyway).

## Configuration of GasChromino Software

The GasChromino program utilizes a configuration file, GasChromino.cfg, to hold important information about the program that the end user may want to modify. The typical global location for this file is /Library/Application Support/GasChromino, although installations may differ (see Installation).

The first time that GasChromino is run, the GasChromino.cfg file is opened for the user to edit. These instructions are also opened. Follow the instructions below for this initial editing. Further information about personalizing the installation and the structure of the GasChromino.cfg file follows.

Initial Configuration for an Instrument The following is a list of the typical changes that will be necessary upon initial installation of GasChromino for an Instrument. These changes are made by editing the GasChromino.cfg file during the setup process. Capitalization is important in the configuration file.

Table 1 Initial Configuration for an Instrument

Configuration option | Explanation
Instrument description
dataStation = False | This installation of GasChromino will run an instrument.
noChannels = 2 | [can be either 1 or 2] Number of Gas chromatography instruments that are hooked up to Arduino box.
instrName = [‘GC 1’, ‘GC 2’] | A list of names for the GC’s. These should be set to something that will make sense to users. The names must be quoted, and the number of names in the list should match the noChannels set above. Names should not be long.
Arduino serial communications
arduinoCom = ‘/dev/cu.usbmodem1421’ | This is the name of the serial usb port on the computer that the Arduino is connected to. This value will most likely change and needs to be determined with Arduino Software. Alternatively, GasChromino has the ability to detect ports that can then be selected within the software, but to set as a default, the GasChromino.cfg file must be edited. See Connection to Arduino.
Defaults for basic experimental variables
timeExper = “1” | This is the time (in minutes) of a GC run. This can be modified to allow for a different default length of run.
comment = “” | This is the default comment that will be added to the data after acquisition.
Processing variables
thresh = 0.001 | This is the default value for the threshold parameter for processing (see Peak Processing tutorial).
gradThresh = 0.0005 | This is the default value for the gradient threshold parameter for processing (see Peak Processing tutorial).
Window visual appearance objects
traceColor = ‘black’ | Color of GC trace
baselineColor = ‘blue’ | Color of calculated baseline
showBaseline = False | Baseline is not shown by default
colorList = ['red', 'orange', 'yellow', 'green', 'blue', 'indigo', 'violet'] | Colors of peak areas highlighted by program. List cycles through colors. Colors can be added or removed or order changed. A single color would be repeated for all peaks.

Initial Configuration for a Data Station The following is a list of the typical changes that will be necessary upon initial installation of GasChromino for an Instrument. These changes are made by editing the GasChromino.cfg file during the setup process. Capitalization is important in the configuration file.

Table 2 Initial Configuration for a Data Station

Configuration option | Explanation
Instrument description
dataStation = True | This installation of GasChromino will not run an instrument, but is only intended to process data.
noChannels = 1 | Since no GC’s are hooked up, there are no channels; however, the Data Station itself counts as one for naming purposes.
instrName = [‘Data Station’] | A name for the Data Station.
Processing variables
thresh = 0.001 | This is the default value for the threshold parameter for processing (see Peak Processing tutorial).
gradThresh = 0.0005 | This is the default value for the gradient threshold parameter for processing (see Peak Processing tutorial).
Window visual appearance objects
traceColor = ‘black’ | Color of GC trace
baselineColor = ‘blue’ | Color of calculated baseline
showBaseline = False | Baseline is not shown by default
colorList = ['red', 'orange', 'yellow', 'green', 'blue', 'indigo', 'violet'] | Colors of peak areas highlighted by program. List cycles through colors. Colors can be added or removed or order changed. A single color would be repeated for all peaks.

Further Configuration Several other options, which most users will not be interested in changing, are available. For completeness, all user modifiable variables in GasChromino.cfg file are included here with commentary. The values in the section DO NOT CHANGE, should not be modified by the user.

Table 3 Complete Configuration Options

Configuration option | Explanation
Instrument description
dataStation = True | This installation of GasChromino will not run an instrument, but is only intended to process data.
dataStation = False | This installation of GasChromino will run an instrument.
noChannels = 2 | [can be either 1 or 2] Number of Gas chromatography instruments that are hooked up to Arduino box.
instrName = [‘GC 1’, ‘GC 2’] | A list of names for the GC’s. These should be set to something that will make sense to users. The names must be quoted, and the number of names in the list should match the noChannels set above. Names should not be long.
Arduino serial communications
arduinoCom = ‘/dev/cu.usbmodem1421’ | This is the name of the serial usb port on the computer that the Arduino is connected to. This value will most likely change and needs to be determined by using the Arduino Software. Alternatively, GasChromino has the ability to detect ports that can then be selected within the software, but to set as a default, the GasChromino.cfg file must be edited. See Connection to Arduino.
timeout = 0.1 | This is the length of time (in seconds) that GasChromino will wait for serial communications with the Arduino.
baudrate = 57600 | Baudrate for serial communication with Arduino. If changed, it must also be changed in Arduino programming.
adcChoice = “ads1115” | Choice for analog to digital converter on the Arduino. The current circuitry only supports this option. If alternate circuitry is provided, this value could be changed (concomitant with changes in the Arduino software) to allow the Arduino multiple options. A previous option of utilizing the Arduino’s native adc is preserved, but not implemented in Arduino software.
adcChoices = {“arduino”: “arduino”, “ads1115”: “ads1115”} | These are the list of choices for adc. Should modifications to the program be attempted, this is where the list of choices would be modified. For further information see source of software.
Defaults for basic experimental variables
timeExper = “1” | This is the time (in minutes) of a GC run. This can be modified to allow for a different default length of run.
comment = “” | This is the default comment that will be added to the data after acquisition.
Processing Variables
thresh = 0.001 | This is the default value for the threshold parameter for processing (see Peak Processing tutorial).
gradThresh = 0.0005 | This is the default value for the gradient threshold parameter for processing (see Peak Processing tutorial).
areaChoice = “trapezoidal” | This is related to the methodology to calculate the area under the peaks. Each peak is treated as a series of small trapezoids. The alternate choice here is “addition” which treats each point in the peak as a simple intensity and the intensities are added up. Trapezoidal integration provides more accurate areas typically.
inBaseCt = 15 | This is the number of points that are included in the running baseline for the automatic peak detection. The baseline value for any point is the average of the previous 15 baseline points. Thus, the program assumes that at the beginning of the trace, the first 15 points do not have a peak in them. Deviations from this assumption will result in poor peak detection.
Window visual appearance objects
traceColor = ‘black’ | Color of GC trace
baselineColor = ‘blue’ | Color of calculated baseline
showBaseline = False | Baseline is not shown by default
colorList = ['red', 'orange', 'yellow', 'green', 'blue', 'indigo', 'violet'] | Colors of peak areas highlighted by program. List cycles through colors. Colors can be added or removed or order changed. A single color would be repeated for all peaks.
mainwindSize = “1500x1200” | Size of main program window “WIDTHxHEIGHT” in pixels
mainwindPos = "50+50" | Position of main program window on initial running from top-left corner of screen.
liveframeHeight = 500 | Initial height of frame for Live data from GC
liveframeWidth = 900 | Initial width of frame for Live data from GC
dataframeHeight = 300 | Initial height of frame for Data
dataframeWidth = 500 | Initial width of frame for Data
mainwindTit = “GasChromino Data Collection Interface” | Title on top of the main program window

## Installation of GCDualInstrumentsSimul (Arduino Program)

The GasChromino hardware utilizes an Arduino Uno (Rev 3) microcontroller to communicate with the gas chromatography instruments. GasChromino units obtained through us are loaded with the appropriate software (GCDualInstrumentsSimul). However, if you are building your own unit or are updating the software, you will need to load the software using the Arduino software. The following are instructions for this process.

1. Obtain and install Arduino Software
  a. Currently available at: https://www.arduino.cc/en/Main/Software
  b. Instructions for installation: https://www.arduino.cc/en/Guide/HomePage
2. Make sure GasChromino hardware is connected to computer by USB cable
3. Open Arduino Software (IDE)
4. Check to make sure that GasChromino’s Arduino is being recognized by the software
  a. Menu item Tools/Port:
5. Add ADS1X15 library to Arduino software
  a. Menu Item Sketch/Include Library/Manage Libraries…

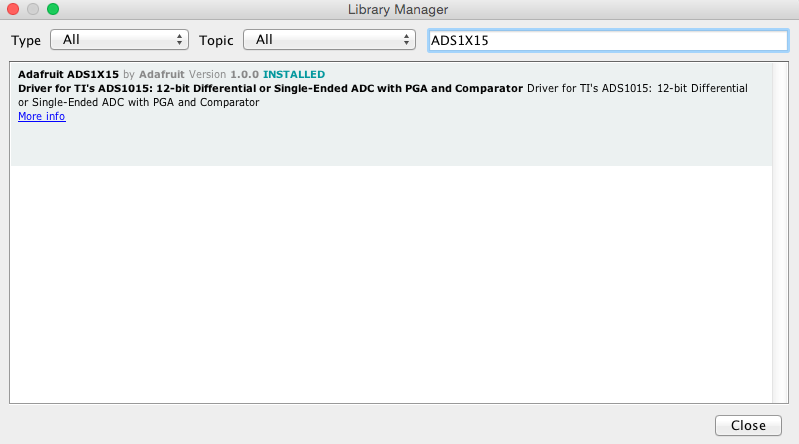
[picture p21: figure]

6. Open GCDualInstrumentsSimul in Arduino Software (IDE)
  a. Default location for GCDualInstrumentsSimul directory: /Library/Application Support/GCDualInstrumentsSimul
7. Upload software to GasChromino hardware
  a. Menu Item Sketch/Upload

The software should now be installed on the GasChromino’s Arduino microcontroller. See Troubleshooting section for (hopefully) solving any problems.

### Troubleshooting

The most likely cause for a failed uploading of the software is that the USB port for the GasChromino has not been identified correctly. See the Arduino instructions for troubleshooting this particular area.

It is also possible that the program has been accidentally edited causing an error in the compilation of the program. If this is the case, the easiest remedy is to re-open the software and try the upload again.

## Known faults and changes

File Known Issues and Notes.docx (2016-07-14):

Known Issues:

Using python within conda environment gives error (which doesn’t affect program):

2016-05-31 10:25:08.756 python[16358:1631704] setCanCycle: is deprecated. Please use setCollectionBehavior instead

This does not happen with iPython, nor does it seem to happen with Python 3.5 installation on Mac. Multiple reports of this error on-line.

Notes about installation:

1. Need to make sure that python 3.5 is installed. (Could check to see if it will run on 2.7)
2. Use pip to install following packages:
  a. Command: pip install pyserial numpy

Pip install

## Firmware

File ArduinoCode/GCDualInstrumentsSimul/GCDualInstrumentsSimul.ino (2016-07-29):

/*
 GC Analog Input
 
 This serves as a simple data capture routine from a
 1.0 V serial output of HP 5890 Series II gas chromatograph.

 Current Version: Complete with two channels, multiple runs, 

 The circuit:
 See Frizzing diagram for description of circuit.  GCAnalogInputCircuitADS2ChanFinal.fzz

 Uses Adafruit breakout of ADS1115 Texas Instruments 16-Bit ADC

 Two different analog signals from GCs can be accommodated simultaneously 

 Each signal has a separate Start/Stop Button
  Signal 1
    A0 input on ADS1115
    Start button on IO pin 9
    Stop button on IO pin 3
    Greed LED on IO pin 6
   Signal 2
    A1 input on ADS1115
    Start button on IO pin 8
    Stop button on IO pin 2
    Greed LED on IO pin 5 

 Based upon Analog Input Example Created by David Cuartielles
 modified 30 Aug 2011
 By Tom Igoe

 GCDualInstrumentsSimul code written by T. Andrew Mobey, 9 Jul 2016
 based upon GCDualInsruments code

 Known Issues:
  
 */
#include <Wire.h>
#include <Adafruit_ADS1015.h>

Adafruit_ADS1115 ads1115(0x4B); // construct an ads1115 at address 0x4B (ADDR connected to SCL)

String channel = "1";          // Default to signal 1
int sensorPin1 = A0;       // input pin for the GC (signal 1)
int ledPin1 = 6;           // output pin for the LED (signal 1)
int sensorPin2 = A1;       // input pin for the GC (signal 1)
int ledPin2 = 5;           // output pin for the LED (signal 1)
float sensorValue1 = 0;    // stores the analog signal potential coming from the GC
float sensorValue2 = 0;    // stores the analog signal potential coming from the GC
float timeValue1 = 0;      // stores the current time
float beginTime1 = 0 ;     // indicate time when the experiment started
float timeValue2 = 0;      // stores the current time
float beginTime2 = 0 ;     // indicate time when the experiment started
boolean writeData1=true;   // whether data should be sent to PC
boolean writeData2=true;   // whether data should be sent to PC
boolean firsttime1=true;   // indicate whether this is the first data point taken (used to set beginTime)
boolean firsttime2=true;   // indicate whether this is the first data point taken (used to set beginTime)
boolean started1=false;    // indicates whether experiment is started yet
boolean stopped1=true;    // indicates whether experiment has been stopped by button
boolean started2=false;    // indicates whether experiment is started yet
boolean stopped2=true;    // indicates whether experiment has been stopped by button
int startButton1=9;        // input pin number for start button (default signal 1)
int stopButton1=3;         // interrupt for stop button (default signal 1)
float timeExper1=0;        // time length of experiment
boolean multiple1=false;
int startButton2=8;        // input pin number for start button (default signal 1)
int stopButton2=2;         // interrupt for stop button (default signal 1)
float timeExper2=0;        // time length of experiment
boolean multiple2=false;
boolean multSet=false;
String startString1="stopped";
String startString2="stopped";
float holdTime = 0.;
String adcChoice="";

void setup() {

  pinMode (ledPin1, OUTPUT);       // declare the various pins utilized as input/output
  pinMode (startButton1, INPUT);
  attachInterrupt (digitalPinToInterrupt(stopButton1), listenForStop, RISING);
  pinMode (sensorPin1, INPUT);

  pinMode (ledPin2, OUTPUT);       // declare the various pins utilized as input/output
  pinMode (startButton2, INPUT);
  attachInterrupt (digitalPinToInterrupt(stopButton2), listenForStop, RISING);
  pinMode (sensorPin2, INPUT);

  
  Serial.begin(57600);
  while (!Serial) {
    ; // wait for serial port to connect. Needed for native USB port only
  }

  ads1115.begin(); // Initialize ads1115
  ads1115.setGain(GAIN_FOUR);
  
  analogReference(INTERNAL);    //Sets analog reference to the Internal 1.1V reference
  
  for (int i=0;i<5;i++){        //Read the analog pin several times to allow it to settle down
     analogRead(sensorPin1);     //after changing the analogReference to internal
  }
  for (int i=0;i<5;i++){        //Read the analog pin several times to allow it to settle down
     analogRead(sensorPin2);     //after changing the analogReference to internal
  }
  
  getExperTime();               //Receive details of experiment from the PC, routine will
                                //wait until it hears from PC
  
  listenForStart();             // Wait until start button is pushed on Arduino
    
}

void loop() {
  if (Serial.available()>0){
    getExperTime();
  }
  
  checkStart();
  
  readGCDataAnalog(adcChoice);
  
  checkTimeOver();
 
  writeDataOrWriteQuit();
  
  if (stopped1&&stopped2){
    resetAndWaitForRestart();
  }
  
  delay(97);  // wait for 97 milliseconds + 3 msec for other routine for ~100 msec recycle time
}

//Procedures to be called

void readGCDataAnalog(String adcCh){
  // reads in analog sensor from gc

  float intervalue=0.;
  float time1=0;
  float time2=0;

  if (started1){
    if (firsttime1){
      beginTime1=millis()/60000.;
      timeValue1=beginTime1;
      firsttime1=false;
    }
    time1=millis();
    for (int i=0;i<10;i++){
      if (adcCh == "arduino"){
        intervalue=intervalue+analogRead(sensorPin1);
      }
      else if (adcCh =="ads1115"){
        intervalue=intervalue+ads1115.readADC_SingleEnded(0);
      }
    }
    time2=millis();
    sensorValue1 = intervalue/10.;
    if (adcCh == "arduino"){
      sensorValue1 = sensorValue1*1.1/1024;
    }
    else if (adcCh == "ads1115"){
      sensorValue1 = sensorValue1*0.00003125;
    }
    else{
      Serial.println("Bad adcCh");
    }
    timeValue1 = ((time1+time2)/120000)-beginTime1;
  }
  
  if (started2){
    intervalue=0;
 
    if (firsttime2){
      beginTime2=millis()/60000.;
      timeValue2=beginTime2;
      firsttime2=false;
    }
    time1=millis();
    for (int i=0;i<10;i++){
      if (adcCh == "arduino"){
        intervalue=intervalue+analogRead(sensorPin2);
      }
      else if (adcCh =="ads1115"){
        intervalue=intervalue+ads1115.readADC_SingleEnded(1);
      }
    }
    time2=millis();
    sensorValue2 = intervalue/10.;
    if (adcCh == "arduino"){
      sensorValue2 = sensorValue2*1.1/1024;
    }
    else if (adcCh == "ads1115"){
      sensorValue2 = sensorValue2*0.00003125;
    }
    timeValue2 = ((time1+time2)/120000)-beginTime2;
  }
}

void getExperTime(){        // This routine retrieves the experimental time number from PC 
  String multString="";
  String startString="";
  while (multString == ""){
    while (Serial.available()<1){}            // Waiting on PC to deliver string.
    multString = Serial.readStringUntil(' ');   // Collect various information from computer: 
    adcChoice = Serial.readStringUntil(' ');
    startString = Serial.readStringUntil(' ');
    channel = Serial.readStringUntil(' ');
  }  
  if (channel == "1"){
    startString1 = startString;
    String inString="";
    int inChar=0;
    while (timeExper1==0){                 //This section of code was adopted from 
      while (Serial.available() > 0){    //StringToFloat example on Arduino site
        inChar = Serial.read();
        if (inChar != '\n') { 
          // As long as the incoming byte
          // is not a newline,
          // convert the incoming byte to a char
          // and add it to the string
          if (inChar==46){
            inString=inString+".";
          }
          else{
            inString =inString + String(inChar-48);
          }
        }
        else {
          timeExper1=inString.toFloat();
        }
      }
    }
  }
  else if (channel == "2"){
    startString2 = startString;
    String inString="";
    int inChar=0;
    while (timeExper2==0){                 //This section of code was adopted from 
      while (Serial.available() > 0){    //StringToFloat example on Arduino site
        inChar = Serial.read();
        if (inChar != '\n') { 
          // As long as the incoming byte
          // is not a newline,
          // convert the incoming byte to a char
          // and add it to the string
          if (inChar==46){
            inString=inString+".";
          }
          else{
            inString =inString + String(inChar-48);
          }
        }
        else {
          timeExper2=inString.toFloat();
        }
      }
    }
  }
}

void listenForStart(){
   while(!started1&&!started2){
      delay(50);
      if(digitalRead(startButton1)==HIGH&&startString1!="stopped"){
        started1=true;
        stopped1=false;
        digitalWrite(ledPin1,HIGH);
        Serial.print(startString1);
        Serial.print(" ");
        Serial.println("stopped");
      }
      if(digitalRead(startButton2)==HIGH&&startString2!="stopped"){
        started2=true;
        stopped2=false;
        digitalWrite(ledPin2,HIGH);
        Serial.print("stopped");
        Serial.print(" ");
        Serial.println(startString2);
      }
      if (started1||started2){
        break;
      }
   } 
}

void checkStart(){
    if(digitalRead(startButton1)==HIGH&&!started1){
      started1=true;
      stopped1=false;
      writeData1=true;
      digitalWrite(ledPin1,HIGH);
    }
    if(digitalRead(startButton2)==HIGH&&!started2){
      started2=true;
      stopped2=false;
      writeData2=true;
      digitalWrite(ledPin2,HIGH);
    }
}

void listenForStop(){
    if(digitalRead(stopButton1)==HIGH){
      stopped1=true;
      timeExper1=0;
      timeValue1=0;
      writeData1=false;
//      sensorValue1=0;
      firsttime1=true;
      digitalWrite(ledPin1,LOW);
    }
    if(digitalRead(stopButton2)==HIGH){
      stopped2=true;
      timeExper2=0;
      timeValue2=0;
      writeData2=false;
//      sensorValue2=0;
      firsttime2=true;
      digitalWrite(ledPin2,LOW);
    }
}

void checkTimeOver(){
  if (timeValue1>timeExper1){
    writeData1=false;
    stopped1=true;
    timeExper1=0;
//    timeValue1=0;
//    sensorValue1=0;
    firsttime1=true;
    digitalWrite(ledPin1,LOW);
  }
  if (timeValue2>timeExper2){
    writeData2=false;
    stopped2=true;
    timeExper2=0;
//    timeValue2=0;
//    sensorValue2=0;
    firsttime2=true;
    digitalWrite(ledPin2,LOW);
  }
}

void writeDataOrWriteQuit(){
  if ((writeData1&&started1)&&(writeData2&&started2)) {
    Serial.print(startString1);
    Serial.print(" ");
    Serial.print(startString2);
    Serial.print(" ");
    Serial.print(timeValue1,5);
    Serial.print(" ");
    Serial.print(sensorValue1,8);
    Serial.print(" ");
    Serial.print(timeValue2,5);
    Serial.print(" ");
    Serial.println(sensorValue2,8);
  }
  else if (writeData1&&started1) {
    Serial.print(startString1);
    Serial.print(" ");
    Serial.print("stopped");
    Serial.print(" ");
    Serial.print(timeValue1,5);
    Serial.print(" ");
    Serial.print(sensorValue1,8);
    Serial.print(" ");
    Serial.print("q");
    Serial.print(" ");
    Serial.println("q");
  }
  else if (writeData2&&started2) {
    Serial.print("stopped");
    Serial.print(" ");
    Serial.print(startString2);
    Serial.print(" ");
    Serial.print("q");
    Serial.print(" ");
    Serial.print("q");
    Serial.print(" ");
    Serial.print(timeValue2,5);
    Serial.print(" ");
    Serial.println(sensorValue2,8);
  }
  else if (stopped1&&stopped2) {
    Serial.print("stopped stopped ");
    Serial.println("q q q q");
  }
  if (stopped1){
    started1=false;
  }
  if (stopped2){
    started2=false;
  }
}
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

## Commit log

2016-07-12 Working pyinstaller.
    Necessary changes: Needed to fix hooks for qt. New hook files stored in
    directory hooks-pyinstaller. Command for pyinstaller requires identifying
    hook directory for use. See this link:
    https://github.com/viotti/pyinstaller/commit/597af5cb01c064620b53ea1ee537e30f56fa481d
    Command is below.
    pyinstaller --onefile --windowed \
    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
    [aapl.csv, data_x_x2_x3.csv, demodata.csv, msft.csv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]
2016-07-13 Included icons, made bash file to move TK and Tcl to correct locations following build by pyinstaller. Changed name of main program to GCArduino.
    pyinstaller GCArduino.spec
    [aapl.csv, data_x_x2_x3.csv, demodata.csv, msft.csv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]
2016-07-14 Added configuration file.
    This consisted of adding new configuration file that contained variables from
    previous gcardglobals.py: GasChromino.cfg
    gcardglobals.py was rewritten to utilize configparser to pull in parameters
    from GasChromino.cfg. This is done by exec(). Need to research potential danger
    of utilizing this method. (Could file be hijacked to insert malicious code?)
2016-07-21 Added logfile functionality, added check for non-existing configuration file in Python code, currently opens Instructions.pdf and GasChromino.cfg in correct location. Need to modify gcSetup to not co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
2016-07-29 Fixed error with Arduino programming that prevented multiple acquisitions after reaching timeout.
